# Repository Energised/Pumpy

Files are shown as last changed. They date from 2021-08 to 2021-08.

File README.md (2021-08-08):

# Design and Manufacture of a Syringe Pump

Research into Free Open Source Hardware (FOSH) has been extremely useful for academics and hobbyists alike. One such area includes the use of a basic linear actuator to create a rudimentary syringe pump. This has its uses in medical operations (palliative care/hospices/chemotherapy), chemical engineering (reactionware, chemical synthesis) and mechanical operation (life science, nanotechnology).

---
## Table of Contents

1. [Syringe Pump v1](./syringe-pump-v1/README.md)
   1. [Build Guide](./syringe-pump-v1/build-guide.md)
   2. [Modifications](./syringe-pump-v1/modifications-from-build.md)
2. [Syringe Pump v2](./syringe-pump-v2/README.md)
   1. [Build Guide](./syringe-pump-v2/build-guide.md)
3. [Electronics](./electronics/README.md)
4. [Testing Suite](./testing-suite/README.md)
   1. [Pump Operation Calculations](./testing-suite/pump-maths.md)
5. [Pump UI](./pump-ui/README.md)
   1. [Kivy GUI](./pump-ui/kivy-design/README.md)
   2. [PyQt GUI](./pump-ui/qt-design/README.md)
6. [Android Application](./android-app/README.md)
   1. [Pumpy App](./android-app/Pumpy/README.md)
   2. [Bluetooth Handler](./bluetooth-handler/README.md)

---
## Project Objectives

My main objective is to build a version of the Open Source Syringe Pump [1], adding several improvements from other projects that build upon it including:

* Upgraded Carriage for simpler bearing insertion and adjustable syringe holders
* Open syringe clamp for easy removal
* Limit switches for automatic position detection
* Ability to withdraw liquid automatically without removing the syringe
* Touchscreen interface using Python and PyQt 5 for basic user-friendly operation
* Android application to interact with the Syringe Pump via Bluetooth

I also plan to discuss the use of Free and Open Source hardware, the history behind medical syringe pumps and
the process by which we can build and program one with a touchscreen interface and Android remote operation for £150.

Overall I hope to show the process of utilising open source hardware and software to build and manufacture a product that rivals current consumer level technology, alongside providing a deliverable that could be put together and operated by a layman.

---
## What are Syringe Pumps?
Syringe Pumps (or Syringe Drivers) are battery powered pumps used to deliver medication into the body at a constant
rate. Patients are usually given them for a number of reasons:

* Nausea or Vomiting
* Difficulty swallowing oral medicine
* To avoid staff giving injected medicines frequently
* Unable to absorb medicines through their gut effectively

They are commonly used with patients receiving end-of-life care but are useful for managing the above symptoms
during any stage of care.

## Building a Pump

There exist many forms of the Open Source Syringe Pump that have been designed and released online. Having researched a number of these I decided upon 2 designs to work with and implement my modifications to. The STL files for 3D printing, BOM (Bill of Materials) and build guides are located in:

* syringe-pump-v1
  - Based on the Open Source Syringe Pump Library
  - Overhauls the electronics from the original design
  - Adds modifications to improve usability

* syringe-pump-v2
  - Upgrades to the Syringe Pump v1
  - Incorporates design elements from Andrey Samokhins design from Thingiverse
  - Larger side supports

The software to utilise each of these is still in development in the pump-ui and stepper-driver-code folders, but will
be combined into one piece of software with settings for both styles of pump.

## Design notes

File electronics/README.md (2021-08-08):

# Electronics for Syringe Pumps v1 and v2

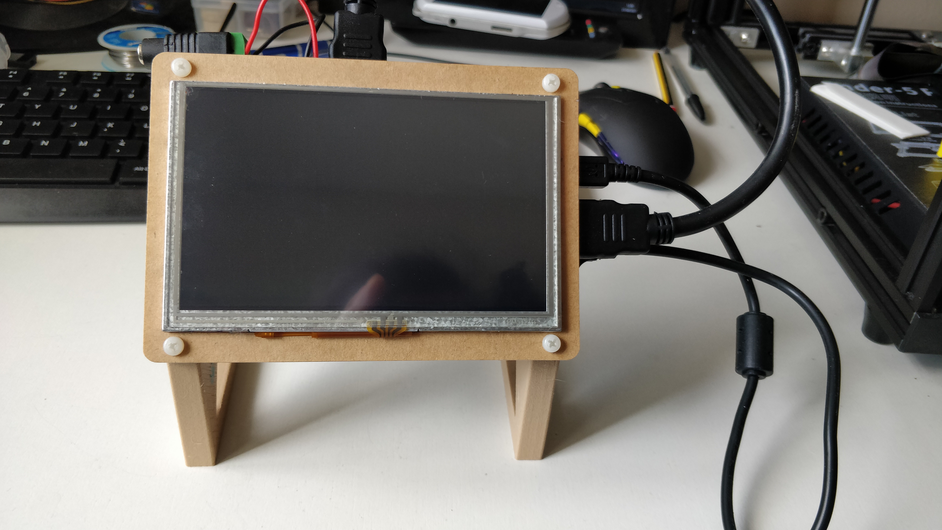
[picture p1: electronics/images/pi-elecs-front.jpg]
Front Image of LCD


To operate the pumps we require the following pieces of equipment:

* Microcontroller - Handles operation logic
* Motor Driver - To control the motor and talk to the microcontroller
* LCD Screen - Provides the User Interface and input
* Power Supply - 12V at 2A to run the motor and 5V at 3A for the microcontroller

For each of these I have chosen:

* Raspberry Pi

  - Powerful microcontroller running Raspbian Linux
  - Has built in Wi-Fi and Bluetooth for updates and remote operation
  - 40 GPIO pins for running external components
  - HDMI output for an LCD display

* A4988 Motor Driver

  - Easy to setup and operate
  - Cheap and powerful
  - Easily replaceable in case of failure

* Waveshare 5 inch LCD Touchscreen

  - Touchscreen capable for handling user input
  - Powered by the Raspberry Pi, no need for an external power source
  - Connects through HDMI and USB, doesn't use any GPIO pins

* 12V 2A Barrel Jack - Powers the Motor

* 5V 3A Micro USB - Extra current required to run Raspberry Pi and LCD screen

---
## Schematic for Syringe Pump v1

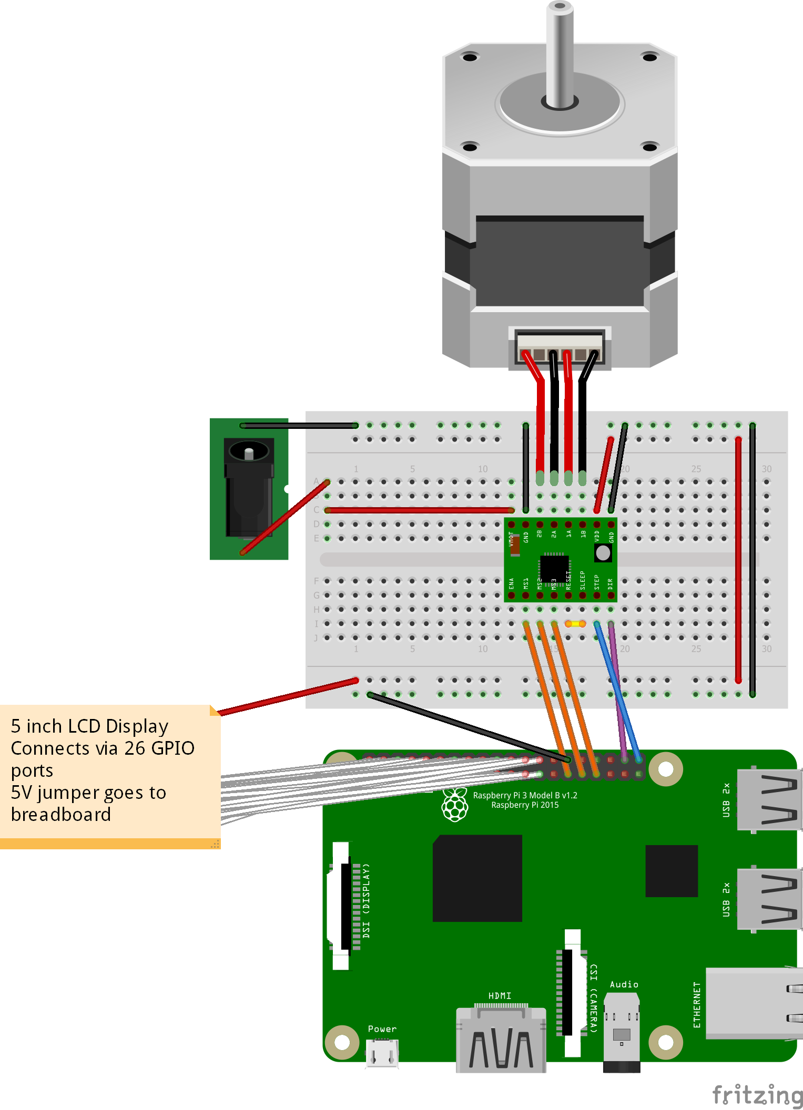
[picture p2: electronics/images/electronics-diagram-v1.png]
Fritzing Diagram for v1 Electronics


---
## Schematic for Syringe Pump v2

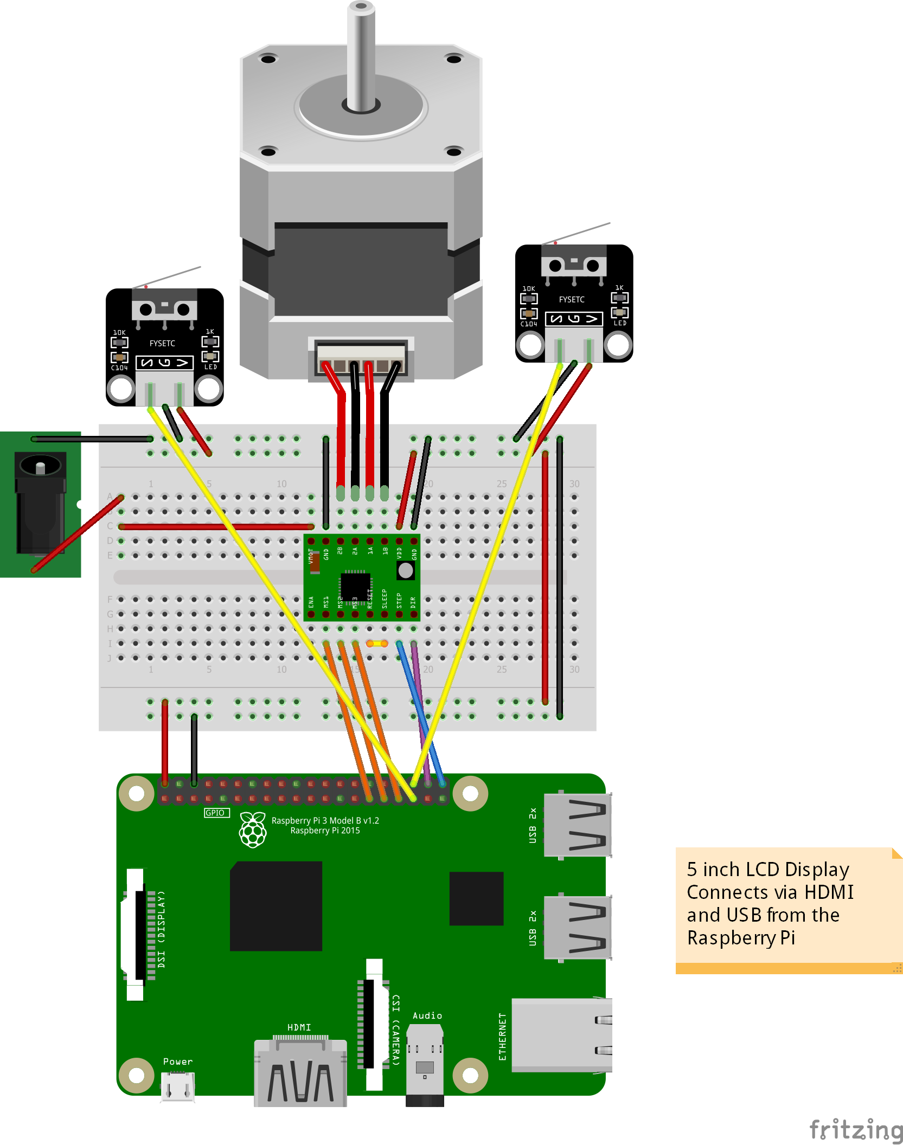
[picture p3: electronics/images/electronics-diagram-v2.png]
Fritzing Diagram for v2 Electronics


---
## Breadboard for v1 Setup

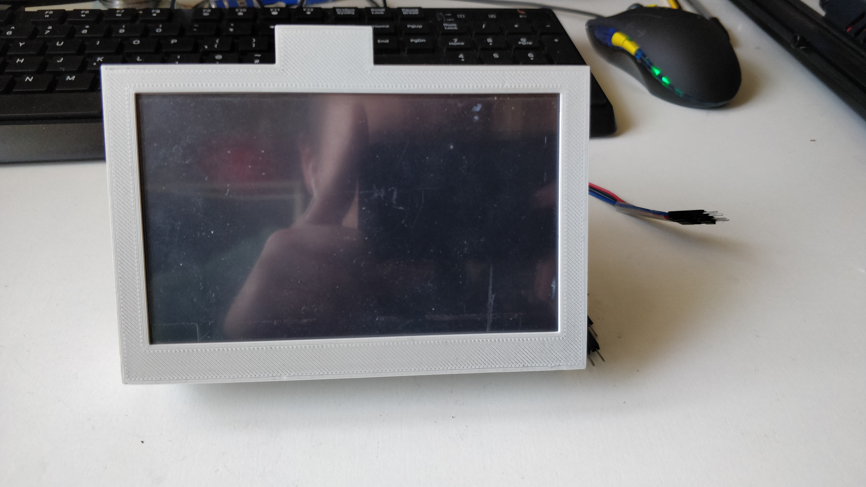
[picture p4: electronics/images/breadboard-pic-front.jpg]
v1 Breadboard with old LCD in 3D printed case

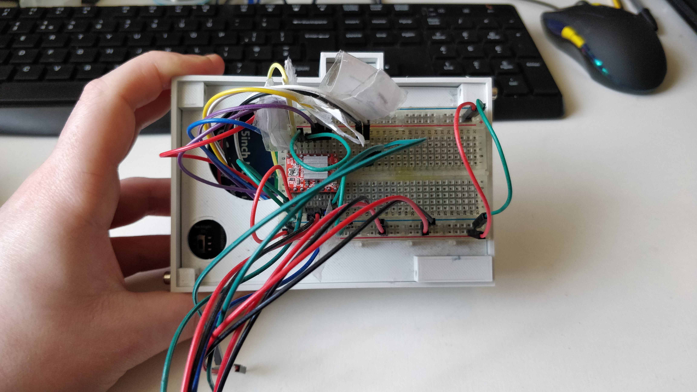
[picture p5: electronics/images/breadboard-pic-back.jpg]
v1 Breadboard system back


---
## Breadboard for v2 Setup

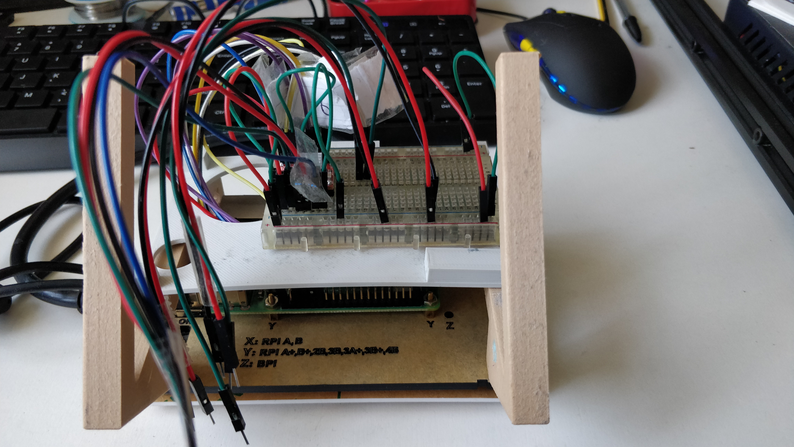
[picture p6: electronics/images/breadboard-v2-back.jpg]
v2 Breadboard back


---
## Final Electronics Setup for v2

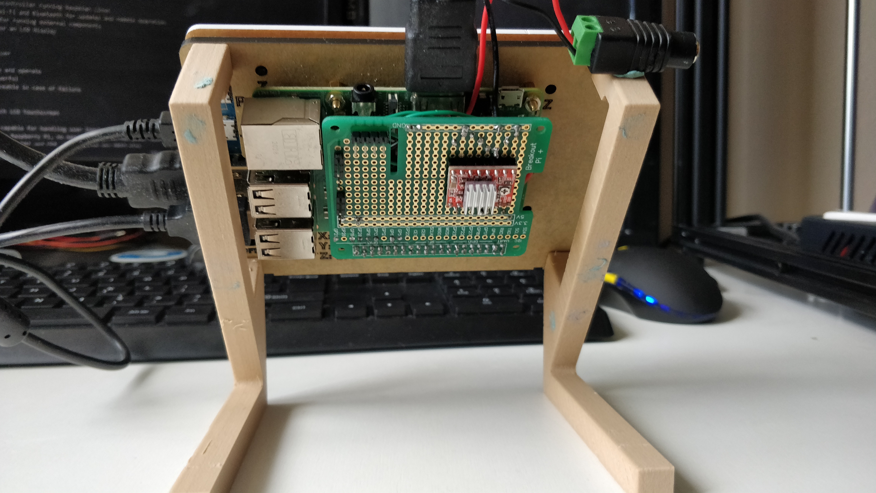
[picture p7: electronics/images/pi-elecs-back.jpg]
v2 Final Back


---
## Notes on Future Upgrades

* Design a PCB based on the breakout board
  - Will mean less soldering is required to build a complete system
  - Can allow for multiple motor drivers and limit switch headers to be installed
* Find a cheaper touchscreen alternative
  - One that makes use of the RPis onboard ribbon cable
* Combined Power Supply
  - 12V 2A for the Motor PSU
  - 5V 3A for the RPi PSU
  - Current system requires 2 power slots where I'd rather have 1

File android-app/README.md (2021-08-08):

# Pumpy - Android Application

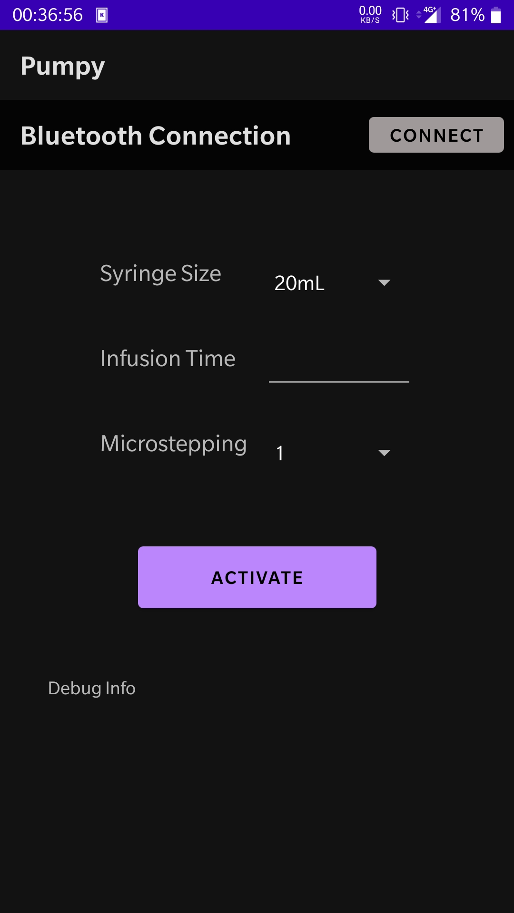
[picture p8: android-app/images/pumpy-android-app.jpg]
Android App Screenshot


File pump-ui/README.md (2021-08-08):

# Building a GUI for Pumpy

Now that we have:

* Upgraded version of the Pump hardware
* Electronics setup with microcontroller and touchscreen interface
* Testing suite for Pump operation
  - Including an object for handling multiple pump operations

We can create a graphical user interface (GUI) that provides all the required functionality
for our pump in a simple design that can be replicated for our Android application.

We've chosen to use Python as our programming language for its compatibility with the GPIO ports
on the Raspberry Pi. It also has a large number of GUI libraries we can make use of such as:

* Kivy
* Tkinter
* PyQt
* wxPython

Here I will discuss the 2 libraries I worked with: Kivy and PyQt5 and why I chose to use
PyQt5 for the final GUI system.

---
## Kivy

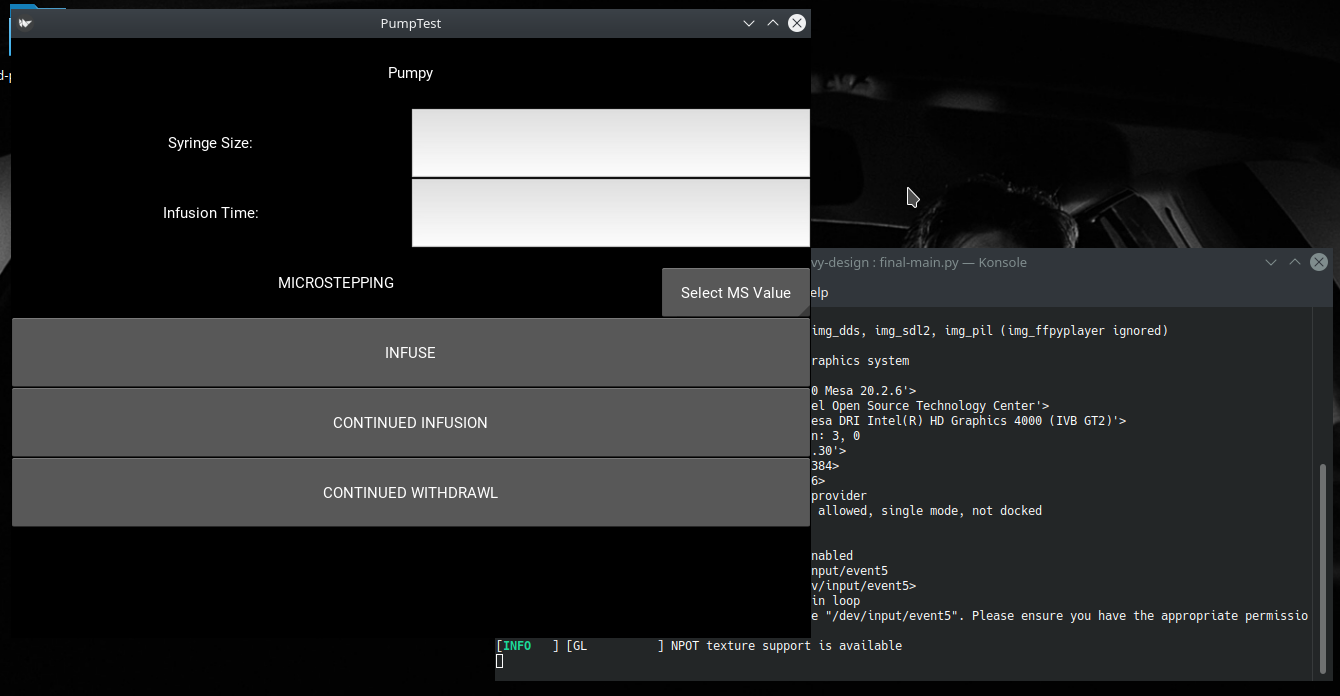
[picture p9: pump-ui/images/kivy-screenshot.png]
Image of Kivy GUI


Documentation for the code can be found [here](./kivy-design/README.md)

There are 2 main ways to design a GUI using Kivy:

* Write a `.kv` file for the UI elements and a `.py` file for the functionality
* Combine UI elements and functionality into a single `.py` file

Using a .kv file requires writing the UI structure in the Kv design language - a tool I
found to be unintuitive. It also allows for the separation of functionality and UI so that
the user can produce easy to read code.

Combining UI elements and functionality into a single file negates this benefit, allowing the
user to write code similar to the JSwing library for Java.

The main benefit of using Kivy is its ability to compile code into an executable Android application
for mobile devices. Doing this preserves the UI design across multiple platforms for consistency and
ease of use.

Unfortunately this also limits the functionality of the mobile application to simple I/O and as such would
be unable to operate the Syringe Pump. Due to this and the unintuitive nature of the Kv design language
I chose to build the application with PyQt5.

---
## PyQt5

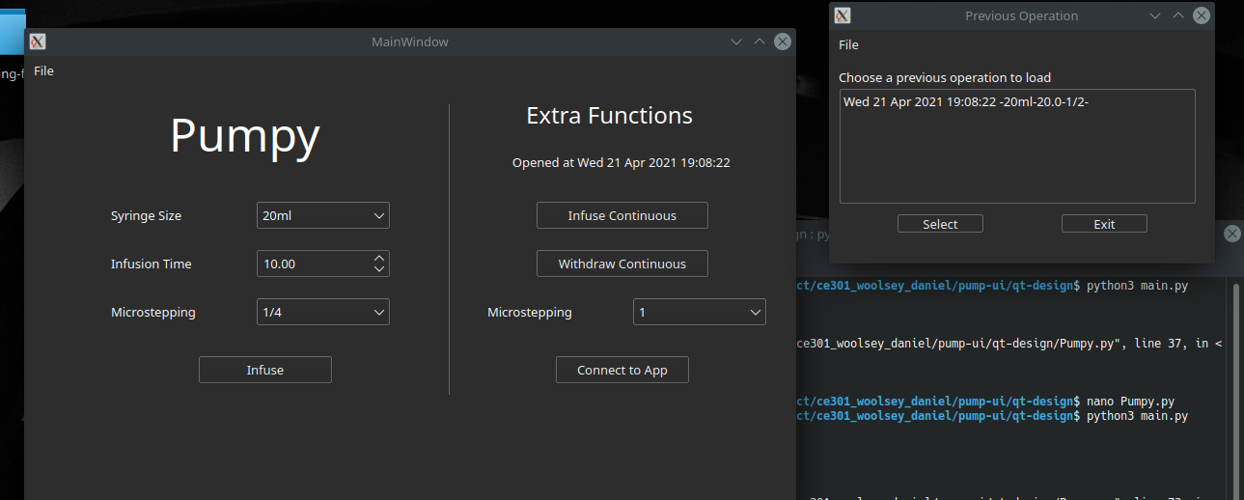
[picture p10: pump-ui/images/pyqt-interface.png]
Image of PyQt5 GUI


Documentation for the code can be found [here](./qt-design/README.md)

The Qt toolkit is a set of cross-platform libraries for software and UI design. The Python Qt library has a
number of tools that make designing UIs easier. For our purposes we use the Qt Designer application to create
a UI in the simplest way possible. This application generates a `.ui` file that can be imported into Python and
from there functionality can be written into the class.

This allows us the separation of UI elements and functionality that Kivy provided us with, but is much more
intuitive for designing a GUI. The Qt Designer gives you the maximum amount of control over how the GUI looks
with instant visual feedback and CSS support for styling elements.

Using this tool along with the PyQt5 library we have written a minimal GUI that is user friendly and adaptable
to mobile devices.

---
## Future Work

* Customisable syringe measurements for different syringe brands
  - Hospitals use a range of Syringe brands and my system is set for BD Plastipak syringes
  - UI would allow a choice of brands and rebuild the lookup table to reflect that
* Debugging tool for testing individual components
  - Would allow for a system where users can easily see what's wrong with their device
  - Very important for a tool designed for use by a computer layman

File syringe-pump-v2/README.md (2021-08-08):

# Syringe Pump v2

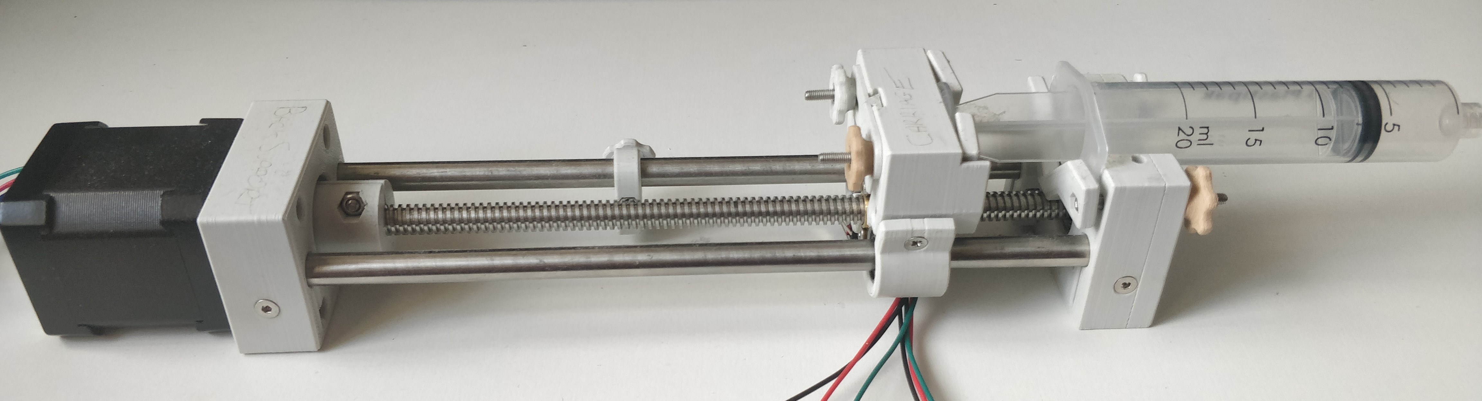
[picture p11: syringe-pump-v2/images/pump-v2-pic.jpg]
Syinge Pump v2 Image


## Introduction

The Syringe Pump v2 is an overhaul of the Open Source Syringe Pump used in Syringe Pump v1 and incorporates
design elements from Andrey Samohkhins Syringe Pump design [1]. This design brings in 2 extra features:

* Custom hand knobs for quick and easy syringe switching
* Limit Switches on the carriage to prevent over actuation
* Adjustable Limit Stoppers for easy withdrawl and setup of syringe

## Build Information

The model files for the 3D printed parts can be found [here](./stl-files) and were printed using an Ender 5 Pro printer. The bill of materials is included below:

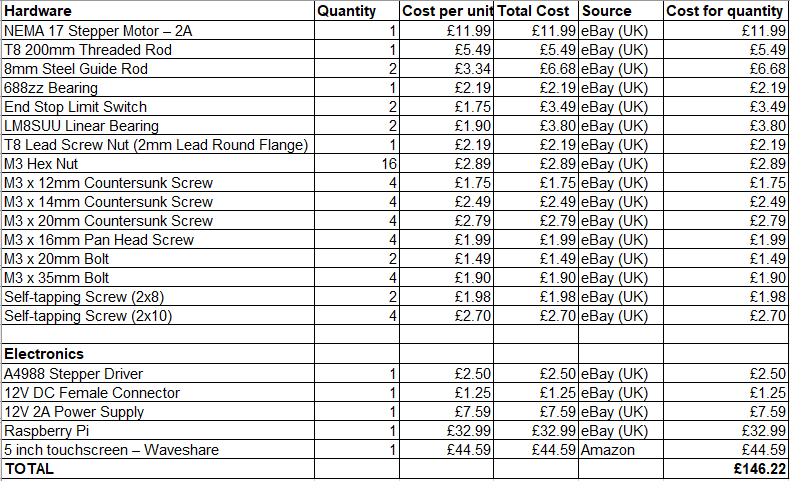
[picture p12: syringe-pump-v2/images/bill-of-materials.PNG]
Bill of Materials


There are a number of electronics requirements for building this pump:

* De-soldering Limit Switches from their breakout boards
* Cutting and soldering wires to each terminal of the Limit Switches

This is easily done with a soldering iron, wires, some solder and a bit of patience.

A [build guide](./build-guide.md) is included to account for modifications to the build guide initially written
for this style of pump. For the full electronics wiring diagrams please refer to the [electronics page here](././electronics/README.md).

## Future Modifications

* More robust hand knobs with locking systems for the bolts
  - Currently we're super gluing the bolts into the hand knobs, but it could be better
* Attachments on the side of the Motor and Idler ends to link with another Pump
  - Also requires extension of the electronics, Pump UI and mobile app

## References

[1] https://www.thingiverse.com/thing:4194094

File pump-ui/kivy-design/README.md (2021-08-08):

# Kivy Design

Screenshot of final-main.py

## `old_main.py`

This class was developed as a test system for trying out each of the UI elements required
for the Pumpy UI

### Functions

```
def forwards(instance)
def backwards(instance)
def release(instance)
```

Test functions to ensure that binding functions to elements works as intended

### Class

`def PumpTestApp(App)`

Main class to encapsulate all functionality and elements of the application. Subclasses the
App object from the Kivy library: `kivy.app.App`

### Methods

`def build(self)`

Overridden method inside of `PumpTestApp` that sets up 3 layouts:

* `main_layout`
* `middle_layout`
* `middle_left_layout`

Labels and buttons are setup inside of these layouts. `on_press` and `on_release` variables
for each button are set to the functions defined above. This method then returns `main_layout`
which is executed in the main function of the program.

### Main Method

```
if __name__ == "__main__"
    PumpTestApp().run()
```

The `run()` method of the App class will take the return value of the `build()` method and run
the layout through its graphics processing engine in order to generate the GUI we've described.

---
## `final-main.py`

Built to try a different layout style and build in the necessary features for the pump to be
operated

### Functions

```
def forwards(instance)
def backwards(instance)
def release(instance)
```

Test functions to be bound to buttons on the GUI

### Class

`def PumpTestApp(App)`

Main class that subclasses App and contains the methods for running the UI

### Variables

```
size_input = ObjectProperty()
time_input = ObjectProperty()
ms_button = ObjectProperty()
```

Objects to store widgets (UI elements) so we can call on them for the given user input or choices
for use by Pumpy.

### Methods

`def infuse(self, instance)`

Takes the given values for syringe size, time and microstep and displays them to the screen - these
values can easily be sent to Pumpy for infusion

`def show_spinner_value(self, spinner, text)`

Method for getting the value of a given spinner - a spinner is a clickable widget that allows the user
to input a number without typing

`def build(self)`

Sets up 4 layouts along with inputs for syringe size, microstepping and time input. Then buttons are set up
for infusion, continuous withdrawal and continuous infusion. The functions and methods above are bound to these
buttons and the UI returns the layout `main_layout`

### Main Method

```
if __name__ == "__main__":
    PumpTestApp().run()
```

The `run()` method of the App class will take the return value of the `build()` method and run
the layout through its graphics processing engine in order to generate the GUI we've described.

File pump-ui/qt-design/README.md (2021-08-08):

# PyQt Design

## `ui/pumpy-2.ui`

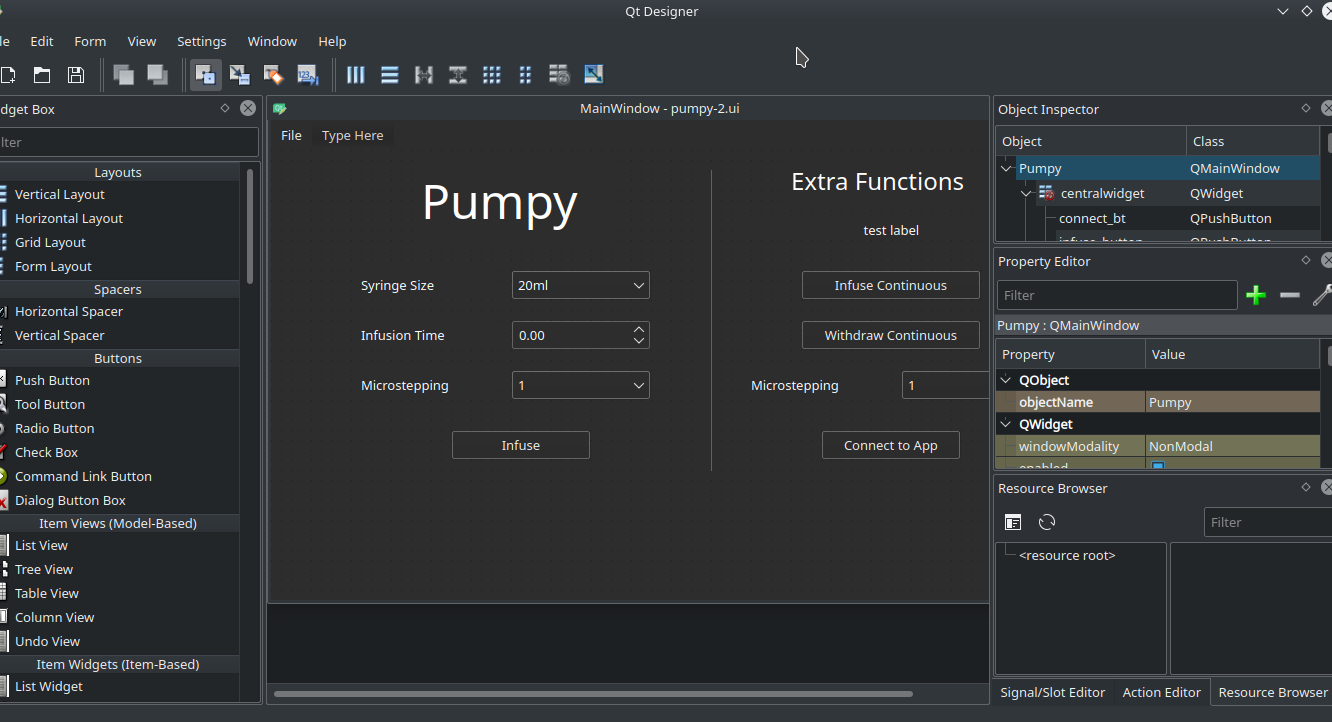
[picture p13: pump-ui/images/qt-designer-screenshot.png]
Image of Qt Designer


This is an image of the UI designed in Qt Designer - this is the second iteration I
wrote for this UI. Using stylesheets with Qt Designer brings some issues with elements
in the layout hierarchy so where the background should be grey it can show up white.

## `ui/prev_op.ui`

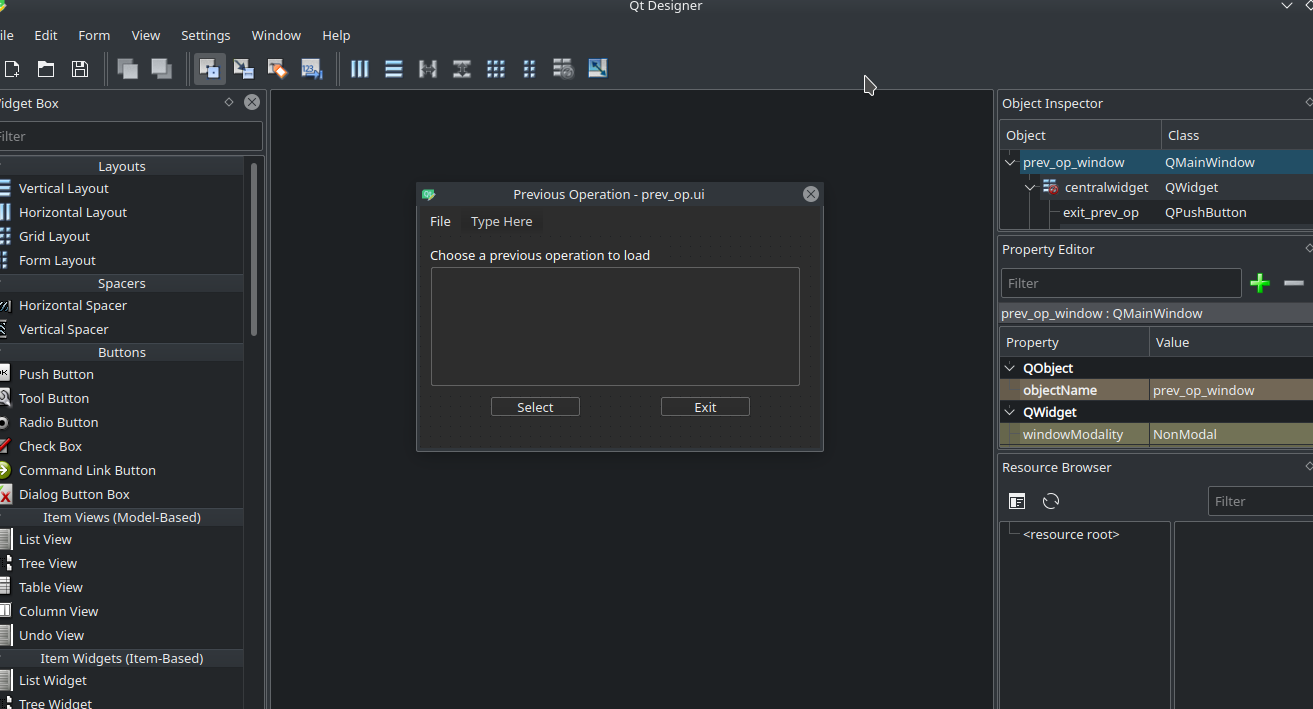
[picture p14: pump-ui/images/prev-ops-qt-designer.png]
Image of Qt Designer


Same issues as above were present, but this menu option is much simpler.

## `main.py`

### Classes

`class Pumpy_Ui(QtWidgets.QMainWindow)`

Handles importing the UI file, encapsulates the functions that the UI must perform and
assigns them to the correct buttons and text input elements.

`class PreviousOperations_Ui(QtWidgets.QMainWindow)`

Performs the same functions as above but for the Previous Operations screen

### Methods

For `Pumpy_Ui()`:
---

`def __init__(self)`

Imports the UI file `pumpy-2.ui`, sets up the Pumpy instance, connects functions to
appropriate buttons, sets up previous operations list and displays the window

`def infuse_button_pressed(self)`

Takes the user input values and calls `self.pump.pump()` with those values as
arguments - work is being done on a threaded alternative so that the GUI can
still be used while the pump is running

`def infuse_continuous_pressed(self):`

Takes the user defined micro-stepping value and runs the `self.pump.continuous()`
method for that value with `Pumpy.INFUSE` as the direction argument

`def withdraw_continuous_pressed(self)`

Takes the user defined micro-stepping value and runs the `self.pump.continuous()`
method for that value with `Pumpy.WITHDRAW` as the direction argument

`def open_prev_ops(self):`

Initialises the Previous Operations UI class and displays it to the screen

`def load_prev_ops(self, operation)`

When a previous operation is loaded in from the Previous Operations UI, this method
is called to setup the input boxes with the chosen operation

`def exit_ui(self)`

Closes the program by calling `sys.exit(0)`

For `PreviousOperations_Ui()`
---

`def __init__(self, parent)`

Load the Previous Operations UI file, bind functions to buttons and populate the
list of previous operations

`def load_operation(self)`

Gets the selected operation as a list and sends it to the `load_prev_ops(self, operation)`
method in `Pumpy_Ui()`

`def exit_ui(self)`

Closes the window by calling `self.close()`

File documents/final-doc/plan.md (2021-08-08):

# Final Document Planning
---
# Design and Manufacture of a Syringe Pump

## SECTION 1 - BACKGROUND

### Hardware

- 3D Printing
- Electronics
    - Raspberry Pi
        -
    - Motor Driver - A4988
    - NEMA 17 12V 2A Motor
    - Touchscreen
        - Choice of connection: GPIO, Ribbon cable, USB

### Software

- 3D Modelling
- Slicer
- GUI Library

### Medical Hardware

- Commercial Syringe Pumps
- Push for open source hardware (JOGL)
- Current Situation - COVID-19

## INVENTORY

All files I've worked on are included in this GitLab repository, will list below:

### Syringe Pump V1

- STL files (models) of each printed part
- Bill of Materials - all non printed parts and costs
- Datasheets for electronics
- Testing suite (pump_test.py - should separate file into 2 - one for each pump version)
- Build guide (on paper, to be written up in a markdown document)
- Modifications list I wrote to implement for V2

### Syringe Pump V2

- STL files (models) of each printed part
- Testing suite for extra functionality - limit switches to avoid chances of damage
- TODO: Write build guide

### Code
- Testing suite for both pump versions
- Pumpy - Pump operation handler class
- GUI 1 - Kivy version with pump operation code
- GUI 2 - PyQt5 version - better than Kivy, easier design process

### Electronics

- Breadboard version with Elecrow touchscreen
- Breakout board version with USB powered touchscreen (breakout board still failing :/)
- Breadboard with USB powered touchscreen - best alternative currently

## REFERENCES

Science - Pandemic brings mass vaccinations to a halt
Kheiralla et al. - Design and Development of a Low Cost Semi-Automated Poultry Vaccination Machine
Iqbal et al. - Automation of Vaccination and Blood Sampling Procedures
WHO. - Framework for decision-making: implementation of mass vaccination campaigns in the context of COVID-19
Gibson et al. - Vaccinate-assess-move method of mass canine rabies utilising mobile technology data collection in Ranchi, India
Amarante at al. - An Open Source Syringe Pump Controller for Fluid Delivery of Multiple Volumes
Kreiger et al. - Environmental Impacts of Distributed Manufacturing frm 3D Printing of Polymer Components and Products
Wijnen et al. - Open-Source Syringe Pump Library
Booeshaghi et al. - Principles of open source bioinstrumentation applied to the poseidon syringe pump system
Pearce - Quantifying the Value of Open Source Hardware Development
Dryden et al. - Upon the Shoulders of Giants: Open-Source Hardware and Software in Analytical Chemistry
Nature - Make nanotechnology research open-source
Baechler et al. - Distributed Recycling of Waste Polymer into RepRap Feedstock
Garcia et al. - Low-cost touchscreen driven programmable dual syringe pump for life science applications
Pusch et al. - Large volume syringe pump extruder for desktop 3D printers
Pearce et al. - Open-Source Wax RepRap 3D Printer for Rapid Prototyping Paper-Based Microfluidics

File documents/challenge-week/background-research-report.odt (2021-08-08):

CE301 – Design and Manufacture of a Syringe Pump

Background Research Report

BENEFITS OF OPEN SOURCE TECHNOLOGY

Open-Source technology has provided academics and hobbyists alike with the tools to bring their ideas to life. Tools such as RepRap [1] , Arduino [2], Apache [3] and Linux [4] have been instrumental in the widespread adoption of open-source in both free and commercial products since the early 1990s. The innovations bought about by these projects are widespread in modern day society: Android devices all have their roots in the Linux kernel, commercial 3D printer design is based on RepRap using Arduino-based control boards and 80% of the top 10 most accessed websites are running their servers on Linux [32].

Economists would have you believe that innovation comes solely from competition within markets: businesses competing to gain the largest profits by creating the best product. This point is antithetical to the philosophy of open-source development [5]. Open-source still allows for businesses to profit from open-source work, depending on the license type a project falls under, but the driving factor is innovation first and foremost – innovation coming from any individual/party with an interest in the research. With the internet allowing information to spread faster than ever before, open-source has the means to fully democratise information and prove that Isaac Newtons famous quote: “If I have seen further it is by standing on the shoulders of giants” is as true today as it was in his day [6].

FOSH (Free Open Source Hardware) has become a popular topic in the last decade, with 3D printing as a driving force to find cost-effective, reproducible solutions to areas such as specialised research equipment. Centralised repositories containing FOSH projects include the Open Hardware Repository [8] (created by CERN) and the dedicated journals HardwareX [9] and Journal of Open Hardware [10]. The greatest boundary to progress for FOSH comes from how a project is licenced. There are 2 classes of open-source licenses:

- Copyleft : Users can redistribute the original work or any derivative work as long as it uses the same license as the original work
- Permissive : Users can redistribute the original work or any derivative work under any license they choose

Copyleft licenses preserve the original works licence through any derivative work – that is work that modifies the original. On the other hand permissive licences allow redistribution of work in any setting: open-source or commercial. Permissive licences allow for large scale implementation of derivative work since the project can be run as a business while still preserving its open-source origins. The best example of this is the Android operating system whose open-source license allows for free application development and distribution – iOS on the other hand charge $99 per year for a developer license [33]. While somewhat counter-intuitive to the idea behind FOSH the proof is in the widespread adoption of Android with a 74% market share for all mobile devices [11].

FOSH requires a self-sustaining community to provide new points of innovation and collaboration – with certain individuals showing up more often. One such individual, Joshua Pearce, has been working in this community for over a decade with notable works such as: Open Source Syringe Pump Library [12], RepRapable Recyclebot [13], Wax 3D Printing for Microfluidics [14], Environmental Impacts of 3D Printed Products [15] as well as articles touting the benefits of adopting open-source in scientific fields such as nanotechnology [16]. His research has been cited over 15,000 times and has inspired many derivative works such as the project I am undertaking. He has written 2 books on the use of open-source technology and is on the editorial board for the journal HardwareX [9]. Without him the FOSH community and my own project would be very different.

3D PRINTING

Starting at the University of Bath back in 2005 the RepRap project intended to create a 3D printer that was low-cost and could print its own parts, eventually becoming a self-replicating machine. Before this project, a 3D printer would cost over £25,000 [1] and used a technique known as FDM (Fused Deposition Modelling) whose patent wouldn’t expire until 2009 [17]. This patent along with several others filed by Stratasys Inc. allowed the company to monopolise the manufacturing process, charging extortionate amounts for printers under a closed license. The expiration of the FDM patent allowed work from RepRap, Ultimaker and other businesses to be commercialised and brought down the cost of printers to £1000 and under [18].

3D printers can work with a variety of materials, most commonly thermoplastics such as PLA, ABS and TPU. A 3-axis gantry holds the extruder and 4 stepper motors controlling X, Y, Z movements and the pushing of material through the extruder. Models are designed using 3D modelling software (e.g. Blender, Maya, OpenSCAD) and run through a slicing program (e.g. Cura, Slic3r, Simplify3D) to generate Gcode – a human readable language instructing the machine where, when and how to move. This toolchain has enabled users – both beginners and experts – to build anything they can design. Websites such as Thingiverse and Youmagine are repositories for model files, allowing users to ‘remix’ the designs they find to suit their own projects and reinforces the open-source platform that RepRap was first build on.

Thermoplastics are just one of many materials 3D printers can be configured to work with. TPU is an example of a flexible thermoplastic, suiting designs that require strong and bendable moving parts. RepRap based printers have been modified to print wax (removing a large number of cost and time intensive processes) [14], hydrogels through syringe pumps that replace the extruder on a regular 3D printer [20], liquid catalysts for small scale 3D printed reactors with comparable purity to traditional glassware reactors [21] and so called ‘smart materials’ such as electroactive polymers that change their size or shape when stimulated by an electric field for fluid motion in robotics [22].

Another factor to consider is the environmental impact of 3D printing. Waste plastics account for 5 million tonnes of waste every year in the UK alone [23] taking hundreds of years to decompose: polluting soils, rivers, oceans and harming animals. The process of upcycling waste plastic has come in many forms: most notably the creations of Spiral and Joyxee Islands, pieces of land supported by around 100,000 plastic bottles [24]. In the context of 3D printing the concept of RecycleBots have gained traction since 2013, which involve the shredding of household plastics (e.g. milk and water bottles, laundry detergent bottles) and extruding them into usable 3D printing filament with a diameter margin of error of <5% [13]. This brings the estimated cost of filament to 2.5 cents per/kg (< 2 pence), less than 1000x the cost of commercial filament. The device itself costs less than $700 (roughly £540), but the return on investment and reduction of individual carbon footprint heavily outweigh this starting cost.

The future of 3D printing hinges on the community of makers working together to show the benefits of this technology to the consumer. Reddit has many useful communities doing this already, such as those dedicated to: helping solve printing issues (/r/fixmyprint), advertising practical prints (/r/functionalprint), advice for every brand of commercial printer (/r/ender3, /r/prusa etc) and lengthy posts detailing the process of choosing a printer all the way to calibration for micrometer-accurate prints [34]. Having bought an Ender 5 Pro for use in my project, the maker community has been a crutch for solving issues I would otherwise have spent days trying to work out myself.

RELATED RESEARCH

Syringe/Infusion Pumps are programmable linear actuators that push a syringe plunger with a set torque over time using a stepper motor. Most stepper motors perform 200 steps per revolution (meaning each step is equivalent to 1.8 degrees) and can be programmed to use microsteps, upping this value to 3200 steps per revolution. Flow rate (usually mesured as micro litres/second) can be calculated theoretically and the pump calibrated to compare actual liquid infused [26]. These devices are simple in concept but must conform to strict health and safety standards before use in a medical setting [35]. For this reason, companies manufacturing these pumps can charge from £300 to over £2000. In a research setting this upfront cost may seem extortionate for a closed-source and difficult to modify piece of equipment. Open-source research into syringe pumps has put the cost to fabricate a custom pump at under £100 [12]. Since the Open-Source Syringe Pump Library (OSSPL) was first released in 2014 its design has been downloaded over 8000 times [27] and many papers exist creating novel uses for it.

Appropedia was used to setup a page detailing the OSSPL and includes a bill of materials along with instructions for building one yourself [19]. As a result a number of modifications were designed and linked to the main project page such as the Lynch modifications [25] which give the pump features similar to those of a commercial pump. Unfortunately the software library the project uses is deprecated and doesn’t run, so we must look at other projects for an operational analysis of the product.

Two such projects exist and I plan to utilise aspects from both that fit with my concept of an open-source syringe pump:

The low-cost touchscreen driven programmable dual syringe pump (PDSP) is designed for laboratory applications – namely for (in laymans terms) breaking down cells into lysates (liquid protein from cells) for analysis, a process that would ordinarily be done by hand [26]. The design of the syringe pump is inspired by the OSSPL with a focus on user interaction via a touchscreen interface. The paper contains a great deal of information on the building process, making effective use of images to help guide anyone attempting to replicate the project. The design is extensible through the use of the PiPlates MotorPlate: on its own capable of controlling 2 stepper motors, extended up to 16 stepper motors by adding more MotorPlates for larger scale systems. The printed design files and software are easily available online, with the interface being easily re-designable with a basic knowledge of Python and Tkinter. From this project I hope to utilise a similar touchscreen interface and provide a similar option for the addition of more pumps.

The Poseidon syringe pump and microscope system is designed for microfluidics experiments – infusing liquid in the order of tens of microns in size [28]. The combination of syringe pump and microscope is for performing basic light microscopy (visualising fine details by focusing a beam of light through a series of glass lenses). The syringe pump itself operates through an Arduino while the microscope operates through a Raspberry Pi, with data being sent via serial communication between the 2 devices to operate the pump on the Pi. From my experience, this can be a slow and impractical method of controlling a motor and is not something I would utilise. The paper uses the Poseidon system to illustrate open-source design principles including: Functionality, Robustness, Safety, Simplicity, Modularity, Benchmarking and Documentation. This is an excellent method of describing an open-source project and I plan to follow the same set of principles with my own work. The design files and code are available on their Github page [29] and includes videos, testing data and the ability to raise issues via Github for easy modification and integration into the project. The principles this project follows should be mandatory for any open-source project.

More trivial concepts have been realised based on the OSSPL such as the 8ARM: Open Source Precision Pump [30] – an interesting take on using syringe pumps and mechatronics to create a robotic bartender capable of mixing drinks to a degree of accuracy no human could recreate even with an error of 1 +- 0.05 cL. While an amusing concept, in practice there are many environmental variables the designer cannot account for. There is also a YouTuber known as Dr D-Flo who designed and build a ‘3D Food Printer’ [31]. This system is a CNC gantry with a syringe pump as an extruder that pipes icing onto a cake or large cookie. Initially using the CNC gantry for a larger print area, he encountered problems using NEMA 23 motors with a stepper driver that couldn’t provide enough current. The project hasn’t been fully realised, but would be an interesting project for independent cake businesses to get an edge over their competition.

REFERENCES

[1] The RepRap Project https://reprap.org/wiki/ (https://reprap.org/wiki/About)A (https://reprap.org/wiki/About)bout (https://reprap.org/wiki/About)

[2] Introduction to Arduino https://www.arduino.cc/en/Guide/Introduction

[3] Apache HTTP Server Project http://httpd.apache.org/

[4] The Linux Foundation https://www.linuxfoundation.org/about/

[5] The Open Source Definition https://opensource.org/docs/osd

[6] Dryden et al. Upon The Shoulders of Giants: Open Source Hardware and Software in Analytical Chemistry Anal. Chem. 2017, 89, 4330-4338

[7] Pearce, J M – Open Source Lab (2013) – ISBN: 978-0-12-410462-4

[8] Open Hardware Repository (CERN) https://ohwr.org/welcome

[9] HardwareX – Elsevier - https://www.journals.elsevier.com/hardwarex

[10] Journal of Open Hardware - https://openhardware.metajnl.com/

[11] Mobile OS Market Share (Accessed October 2020) - https://gs.statcounter.com/os-market-share/mobile/worldwide

[12] Wijnen et al. - (2014) – Open-Source Syringe Pump Library

[13] Woern er al. - (2018) - RepRapable RecycleBot: Open Source 3D printable extruder for convering plastic into 3D printing filament

[14] Pearce et al. - Open Source Wax RepRap 3-D Printer for Rapid Prototyping Paper-Based Microfluidics

[15] Kreiger et al. - Environmental Impacts of Distributed Manufacturing from 3D Printing of Polymer Components and Products

[16] Pearce J – Nature Vol. 491. 519-521- Make nanotechnology research open-source

[17] FDM Patent – Stratasys Inc - https://patents.google.com/patent/US5121329

[18] https://medium.com/@erinwinick/3d-printings-30-year-history-and-why-it-is-popular-now-5200ab21a7ed

[19] https://www.appropedia.org/Open-source_syringe_pump

[20] Pusch et al. - Large volume syringe pump extruder for desktop 3D printers

[21] Combining 3D Printing and Liquid Handling to produce User-Friendly Reactionware for Chemical Synthesis and Purification

[22] Liu et al. - 3D Printing of Smart Materials: A review on recent progresses in 4D printing

[23] https://commonslibrary.parliament.uk/research-briefings/cbp-8515/

[24] https://www.atlasobscura.com/places/joyxee-island

[25] http://www.appropedia.org/Lynch_open_source_syringe_pump_modifications

[26] Garcia et al. - (2018) – Low-cost touchscreen driven programmable dual syringe pump for life science applications

[27] Syringe Pump STL Files - https://www.youmagine.com/designs/syringe-pump

[28] Booeshagi et al. (2019) – Principles of open source bioinstrumentation applied to the poseidon syringe pump system

[29] Poseidon Syringe Pump System – Github - https://github.com/pachterlab/poseidon

[30] 8ARM: Open Source Precision Pump https://www.diva-portal.org/smash/get/diva2:915985/FULLTEXT01.pdf

[31] Dr D-Flo – 3D Food Printer - https://www.drdflo.com/pages/Projects/3D-Food-Printer.html

[32] https://peacocksoftware.com/blog/what-server-os-are-top-sites-running-2020

[33] https://developer.apple.com/support/compare-memberships/

[34] https://www.reddit.com/r/3DPrinting/wiki/gettingstarted

[35] https://www.fda.gov/media/116949/download

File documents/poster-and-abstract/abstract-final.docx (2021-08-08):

Project Title: Pumpy – Design and Manufacture of a Syringe Pump

Student: Daniel Woolsey

Supervisor: Nick Zakhleniuk

Abstract.

Due to COVID-19, medical equipment and PPE have been in short supply and high demand. For the first time hospitals relied on individuals to 3D print face masks to handle the growing supply concerns they faced. This has the potential to be applied to other forms of medical equipment such as syringe pumps, which provide continuous, hands-free drug delivery and can cost more than £1500 per unit.

In this project we designed, 3D printed and built a medical-use syringe pump and computer interface based on Joshua Pearce’s Open Source Syringe Pump. We programmed both a touchscreen interface for a Raspberry Pi computer and an Android application for remote operation via Bluetooth.

We have demonstrated that medical-use syringe pumps can be built for less than 10% of their market value. This open-source approach to manufacturing equipment can allow hospitals to handle supply issues internally and can help to provide inexpensive medical equipment to poor areas with limited modern technology.

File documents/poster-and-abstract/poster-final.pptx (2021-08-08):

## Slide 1

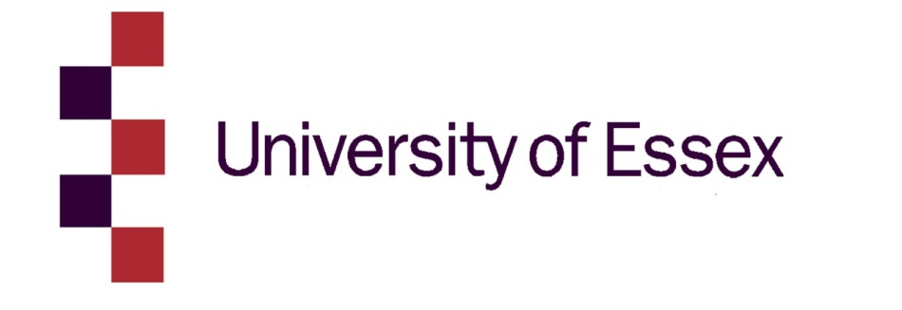
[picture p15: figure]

Pumpy
Design and Manufacture of a Syringe Pump

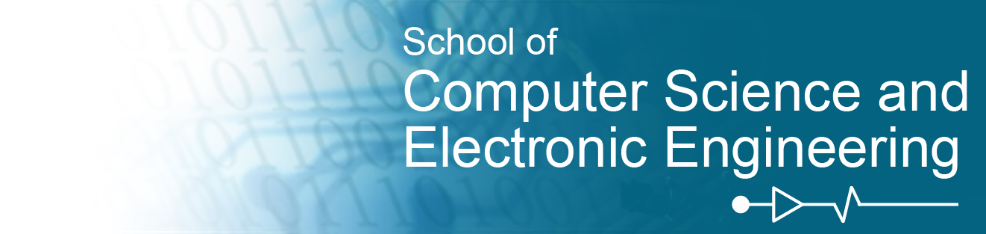
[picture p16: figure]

Student: Daniel Woolsey
Supervisor: Nick Zakhleniuk

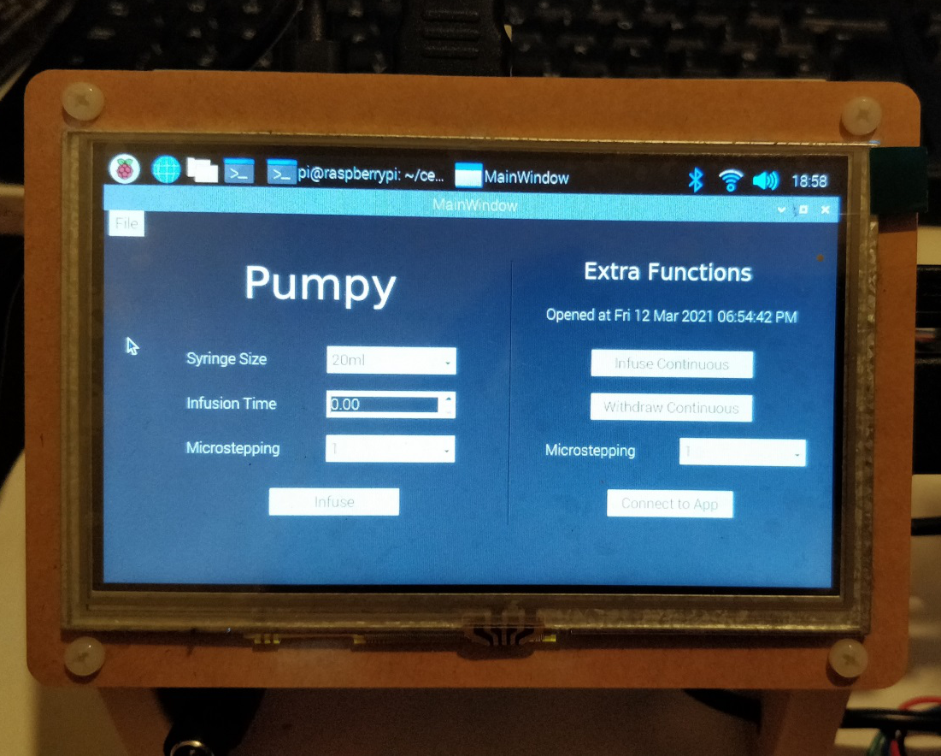
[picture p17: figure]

- Stepper motor for precise movement
- Mostly 3D printed parts to reduce cost
- Hand knobs for easy syringe replacement
- Limit switches on the carriage prevent
damage to the pump

AIM
To build a touchscreen ready, mobile phone controlled, cost-efficient, open source Syringe Pump for a real-world medical applications (estimated costs under £150)

BACKGROUND
- Typical medical-use Syringe Pumps cost > £1000
- Medical equipment is in short supply due to COVID-19
- Open-source Syringe Pumps have only been used in bespoke labs
- 3D printing has paved the way for democratised production
- Eventually, hospitals could print their own equipment
- The approach and the product can be used in areas with limited access to modern technology

- Minimal User Interface
- Wi-Fi and Bluetooth
Compatible
- Powered by a Raspberry
Pi computer
- Touchscreen interface
- Stored backlog of previous
operations

Android application for remote
pump control

Connects to the Raspberry Pi
over Bluetooth

All remote operations are stored
on the pump

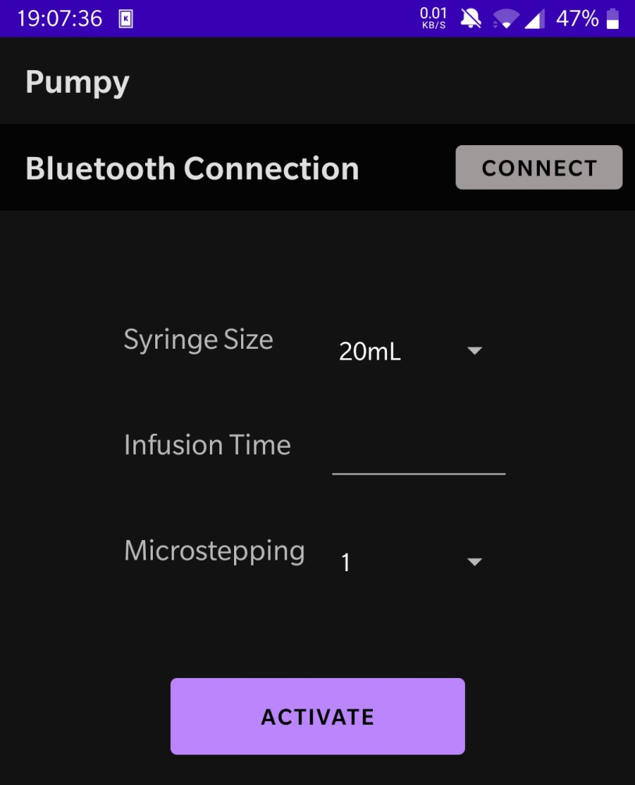
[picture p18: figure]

RESULT
We have demonstrated and implemented a 3D printing-based approach to the manufacture of Syringe Pumps for a variety of medical applications

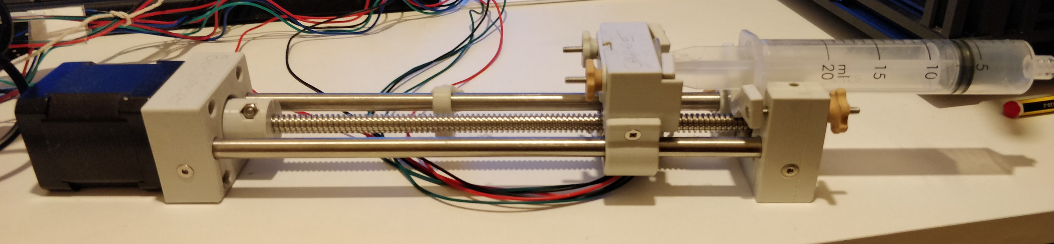
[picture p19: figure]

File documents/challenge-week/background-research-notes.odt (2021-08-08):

notes:

section 1:

- Bringing manufacturing and design to the consumer
- Widespread adoption of popular open source projects
  - RepRap [https://reprap.org/wiki/Wealth_Without_Money]
  - Arduino [https://www.arduino.cc/]
  - Apache [https://www.apache.org/theapacheway/index.html]
  - These have been implemented in both FOSS/FOSH projects as well as consumer products licenced under a permissive license agreement
- Innovation doesn’t come from market competition alone
  - Freedom of information allows for a wider community to become part of the innovation process
  - [Open Source Lab + Upon the Shoulders of Giants]
- Open source licenses exist to explicitly inform users what they can do with the project
  - Copyleft vs Permissive
    - Production of application binaries for commercial use based on open source work
- Patent filing is the greatest hindrance to progress in Open Source communities
  - [Make Nanotechnology research Open source]
  - Large number of Syringe Pump patents filed, lasting 15 years
- Big thanks to Joshua Pearce – Open Source hardware pioneer, contributed to hundreds of projects and articles
  - [Make nanotechnology research open source]
  - [Open Source Syringe Pump Library]
  - [RepRapable Recyclebot]
  - Work on quantifying the value of Open Source Technology
    - Provides a mathematical model for calculating market value in 3 areas
      - Downloaded Substitution Valuation
      - Avoided Reproduction Valuation
      - Market Savings Valuation
    - Alongside a case study: applying this model to the OSSPL along with projected figures for 2019
      - Can calculate this myself in 2020 and compare my findings to his predictions

section 2

  - RepRap project
  - Open source project from Uni of Bath
  - Began February 2004
- Use of varied printing materials
  - PLA/ABS – standard plastics
  - NinjaFlex, Ferrofluids, carbon fibre – next stage of consumer manufacturing
    - 3D printing of smart materials, 4D printing, ferromagnetic domains
    - Sources from previous project on Smooth Surface Generation
- 3D Printing + Liquid Handling for User Friendly Reactionware
  - Modified a printer to extrude a liquid catalyst
  - Printed the reactor casing, printed in the catalyst, then printed the rest of the case
  - Done with 2 printers, a syringe pump mounted on a gantry could achieve a similar result
- RepRapable Recyclebot
  - Turning household plastics (milk/water bottles, detergent bottles) into usable filament for a 3D printer
  - Improvements in the technology over the last 7 years – see [J Pearce – RepRapable Recyclebot + Distributed Recycling of Waste Polymer into RepRap feedstock]
  - [Environmental Impacts of Distributed Manufacturing from 3D printing of polymer components and products]
- Open Source 3D printing of OSAT (Open source appropriate technologies) (2010)

section 3

- Touchscreen idea for intuitive user interface
  - [Low-cost touchscreen driven programmable dual syringe pump for life science applications]
- Poseidon Syringe Pump System
  - Biological applications stemming from the RepRap project
  - Microfluidic devices
- Individuals building and improving on the OSSP project [1 Open Source Syringe Pump Library 2014]
  - Appropedia for user designed modifications [Lynch Open Source Pump Modifications]
  - Choice between microcontrollers and motor control boards – Raspberry Pi vs Arduino, A4988 vs DRV8825
  - Benefits of microstepping – accuracy increase? [Hackaday article on microstepping]
- Open-Source Wax RepRap 3D Printer for Rapid Prototyping Paper-based Microfluidics
  - Removing the need for other more time intensive processes (lithography, etc (see paper))
- Large Volume syringe pump extruder for desktop 3D Printers
  - Modification available for any commercial/RepRap 3D printers
  - Applying a different area of science (hydrogels) to the concept of the Syringe Pump
    - Shows how versatile the concept is
- Trivial projects
  - 8ARM: Open Source Precision Pump for bartending
  - 3D Food Printer – Youtuber Dr D-Flow – Syringe Pump attached to gantry for icing cakes/pies

section 4

(probs gonna ignore this section for now, will add to final document)

MARKET ANALYSIS

- Patent filing (get exact figures)
- Market Value for Infusion Pumps and Syringe Pumps (get figs)
- Compare the market to 2014
  - [Quantifying the Value of Open Source Hardware]
- Number of Syringe Pump projects started since 2014 with OSSPL
- PHDUltra Syringe Pump – Harvard Apparatus
  - Marketed with touchscreen – build isn’t modular, touch to customise
  - Software is a black box, no ability to modify code

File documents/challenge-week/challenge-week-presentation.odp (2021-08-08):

## Design and Manufacture of a Syringe Pump

Daniel Woolsey

## Project Objectives

- Improve upon the Open Source Syringe Pump Library
  - Take inspiration from commercial pumps and other projects
- Allow for easy extensibility into dual pump system
- Add the ability to withdraw solutions into the pump
- Design touchscreen interface for ease of operation
- Compare accuracy of different stepper motors and the benefits of micro-stepping
- Current market analysis of Syringe Pumps
  - Compare to predictions made in case study from ‘Quantifying the Value of Open Source Hardware Development

## Project Objectives

- Develop an Android application as another means of operation
- Display use of Jira and the KanBan methodology in developing a project
  MOST IMPORTANTLY
- Show the process of developing an open-source project
  - Best practices to follow
  - Following 7 key design principles

## Design Principles

- Functionality – Develop for an application
- Robustness – Design with variation in mind
- Safety – Communicate hazards to users
- Simplicity – Make easy to source, build and operate
- Modularity – Build independent and individual units
- Benchmarking – Validate with standard protocols
- Documentation – Describe the design completely

## Implementation Plan

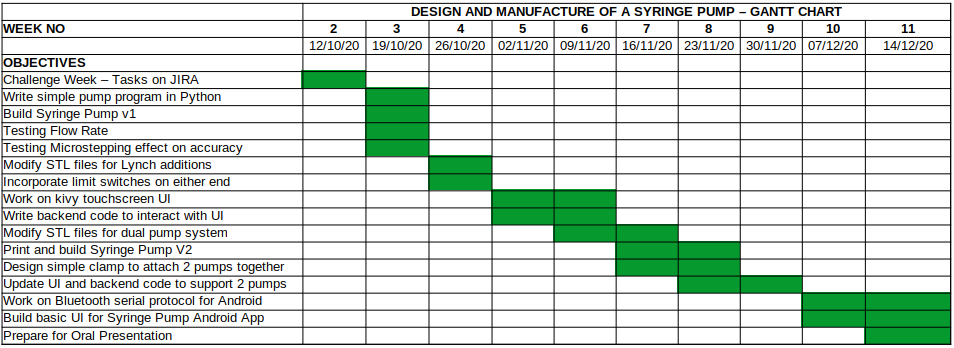
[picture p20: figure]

## Risks

- Lack of novel hardware design changes
  - Software will be novel
- Damage to equipment
  - Everything is cheap and easily replaceable
- With more modifications, project loses simplicity
  - Keep everything modular, get a layman to build and operate the SP based on written documentation

## Context

- Commercial Lab equipment is expensive and unsuitable for modification
  - Open source is inexpensive and (usually) designed with modification in mind
  - The quality of commercial syringe pumps is easily achievable at a low cost
- Updating design for the modern-day user
  - Mobile phones are widespread and easily understood by most everyone
  - Build an interface to reflect mobile app design principles for HCI

## Context

- Quantifying the Value of Open Source Hardware Development
  - In 2014, predictions made about the future of the Syringe Pump market
- Latest Syringe Pump Projects
  - PDSP – Evolved UI and extensibility
  - Poseidon – Focus on micro-fluidics and open-source design principles, strong documentation

## Achievements during Challenge Week

- Applying KanBan methodology to daily project tasks
- 3D printed parts for Syringe Pump and ordered all items on the Bill of Materials
- Timeline of objectives up until Week 11
- Completed Analysis of Related Works for Background Reading

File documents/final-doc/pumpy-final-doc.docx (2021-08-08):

Pumpy – Design and Manufacture of a Syringe Pump

Student: Daniel Woolsey

Supervisor: Dr Nick Zakhleniuk

Second Assessor: Dr Vishuu Mohan

BSc Computer Science

University of Essex

2021

I would like to thank my family and friends for their invaluable support throughout this difficult year.

A big thank you to my supervisor Dr Nick Zakhleniuk whose weekly meetings and consistent guidance helped bring this project to where it is now.

Finally, I’d like to thank the open source community, who have provided resources for anyone to learn and utilise new and interesting technology.

Due to COVID-19, medical equipment and PPE have been in short supply and high demand. For the first time hospitals relied on individuals to 3D print face masks to handle the growing supply concerns they faced. This has the potential to be applied to other forms of medical equipment such as syringe pumps, which provide continuous, hands-free drug delivery and can cost more than £1500 per unit.

In this project we designed, 3D printed and built 2 medical-use syringe pumps based on Joshua Pearce’s Open Source Syringe Pump. We programmed both a touchscreen interface for a Raspberry Pi computer and an Android application for remote pump operation via Bluetooth.

We have demonstrated that medical-use syringe pumps can be built for less than 10% of their market value. This open-source approach to manufacturing equipment can allow hospitals to handle supply issues internally and can help to provide inexpensive medical equipment to poor areas with limited modern technology.

Medical equipment is always in demand yet remains in a status quo – startups with new ideas must work with large corporations to make them a reality. This is due to the difficulty of creating equipment that meets with the approval of regulatory boards worldwide. Large corporations can monopolize specific parts of the market and charge extortionate premiums to the healthcare system that needs it. For example, Johnson and Johnson (JNJ) acquired Auris Health for their Monarch endoscopy robotic system for $3.4 billion [1]. Such a device will become commonplace in hospitals over the next decade but was only able to reach FDA approval after the JNJ acquisition.

Modern equipment like Monarch is a true vision of the future but ignores a huge problem the medical equipment sector faces – the mismatch problem. Outlined in a WHO report from 2010, it explains that the medical equipment industry invests more in R&D for equipment that will only be used in 1st world countries rather than creating accessible, affordable and appropriate equipment for use in low-resource settings [2]. The report hypothesizes that a countervailing force must focus the medical device market towards public health considerations at all stages of the device lifecycle. I believe that open source hardware can be that force.

During the COVID-19 pandemic we saw waves of medical equipment shortages in hospitals worldwide. This led to several open source initiatives allowing individuals to help provide PPE to medical staff such as 3DCrowd [3] and the NIH 3D Print Exchange [4]. Coupled with research into the adoption of open source hardware for diagnostic tools and ventilators [5], we saw hospitals begin to produce their own reusable PPE in-house [6] to handle the supply chain issues they faced. Having seen the benefits of 3D printing and open source hardware in hospitals, there is a chance that open source can be a new norm in the medical industry.

The open source ecosystem is, by nature, decentralized and democratic [7], which goes against many business practices where ideas are patented, and their inner workings are hidden trade secrets. The switch to open source brings product development to the people, with democratic decision making leading to rapid innovation. We’ve seen this with software like Linux, Android, and Arduino – all of them open source projects used in commercial products and provide a better experience for both developers and consumers.

When applying the open source methodology to more complex medical equipment than PPE we are faced with a big issue – regulation. Medical authorities such as the FDA provide resources for manufacturers to follow when attempting to get a device approved for use [8]. Applying this approval process to open source where change and innovation are prioritized is a challenge, since any revisions will have to be re-approved. To overcome this, any open source medical device requires a medically approved baseline with changes approved by committee in regular intervals.

In this paper I want to analyze and build upon an already existing open source baseline for a complex medical device – a syringe pump. Syringe Pumps (also known as Infusion Pumps or Syringe Drivers) are motorized linear actuators that deliver medicine to a patient at a constant rate over a 24-hour period [9]. They are commonly used for patients who have trouble taking medication orally or are in end of life care.

The main goals of this paper are as follows:

- To analyze, build and test a current open source Syringe Pump
- Modify and improve the hardware
- Design an electronics system for user friendly operation
- Create a mobile application for remote pump operation
- Explore the viability of a cheap and open source medical Syringe Pump solution

In Section 2 I explore the background of the main areas the project concerns: Syringe Pumps (both commercial and open source), Open Source technology, 3D Printing and the medical uses of Syringe Pumps along with their issues. Section 3 shows my technical documentation for the project hosted on Gitlab. Section 4 explains how I approached each stage of hardware and why I chose the solutions I did. Section 5 describes my approach to software – the chosen programming language, libraries I decided upon and how they were utilized. Section 6 details the process of my work from building the first prototype to creating a final solution. Finally, in Section 7 I discuss the results and performance of my Syringe Pump system, the project planning and development strategies I used, the benefits and weaknesses of open source development and the future viability of open source medical devices.

This project builds upon previous Syringe Pump projects with a focus on using open source hardware and modern manufacturing processes to bring cheaper medical equipment to the healthcare industry. Below I discuss the main aspects of my project: Syringe Pumps, Open Source, 3D printing and the history of medical Syringe Pumps.

# 2a. Syringe Pumps

Syringe Pumps are used in a variety of contexts. In medicine, they are used to deliver medicine at a constant rate under the skin, helping to manage symptoms such as pain, nausea, and vomiting [9]. In laboratories, they are used to automate routine life science experiments that are taxing to perform by hand [10] or for microfluidics experiments where precise flow rate control is necessary [11]. Syringe Pump prices range between £300 and £2800 [12] for what appears to be a simple piece of equipment. Medical equipment businesses can charge a high price for 2 reasons:

- Cost of getting a medical device approved by regulatory boards such as the FDA and MHRA
- Lack of market competition

For laboratory work, this price point was too high to warrant buying many of them. To solve this problem, scientists have turned to open source hardware to build extensible Syringe Pumps tailored to the work being done

Back in 2014, a group from Michigan Tech University released the Open-Source Syringe Pump Library (OSSP). They provided a proof of concept for a 3D printed Syringe Pump that costs £70 that performs better than most commercial Syringe Pumps in terms of speed and force but is not as accurate as more expensive models [12]. The 3D printed files, bill of materials and build guide were made available for users to build and modify on Appropedia [13] and has been downloaded almost 9000 times [14]. The pump itself is a proof of concept, so members of the open source community have designed modifications to improve on the original design. One such project is the Lynch Pump Modifications that provide a new carriage and syringe holder that are vastly superior to the original designs [15].

There are 2 interesting papers that have built upon the OSSP for specialized use cases in laboratories: The Programmable Dual Syringe Pump (PDSP) and the Poseidon Syringe Pump and microscope.

The PDSP fuses together 2 OSSPs to automate laboratory work in life science applications. More specifically, infected blood cells are infused from one pump to another via a homogenizer. The homogenizer breaks down these cells into their liquid protein constituents with each infusion through it. This process is repeatedly done by hand and allows scientists to analyze the structure of blood cells. Doing this process by hand led to user-dependent variation in the results and damage to the equipment as pressure was applied unevenly [10]. Using the OSSP with a Raspberry Pi controller and a touchscreen interface, they designed a GUI in Python with Tkinter. This system is fully customizable for up to 16 pumps working concurrently and can be used in other areas of lab work.

The Poseidon Syringe Pump is a modified OSSP that incorporates a microscope to perform experiments on microfluidic devices where liquid is infused into systems as small as 10 microns wide [11]. These experiments require a flexible device that can provide precise flow rate control and allow the user to customize the operation software for their use case. Commercial syringe pumps are inadequate for this task since their software is closed source and limited. The pump itself is driven by an Arduino microcontroller that receives software calls from a Raspberry Pi with a touchscreen interface. The GUI is written in Python and uses the PyQt library.

Systems such as the 2 described show that there is a need for a cheap and customizable alternative to commercial syringe pumps. There exist some trivial projects that incorporate syringe pumps into robotic mechanisms such as the 8ARM Precision Pump. This mechatronics system acts as a robot bartender capable of mixing drinks to a high degree of accuracy, around 1 +- 0.05 cL. Although this is an interesting concept there are many environmental variables that the system cannot account for [16].

Open Source is a blanket term for many different criteria that can be applied to anything people can modify and share because its design is publicly accessible. These criteria include free redistribution, access to source code and allowance for modification and derivative works [17]. Use of the term open source began in software around 1990, where development shifted from large scale and rigid waterfall models to iterative development styles like Agile. This change brought about more democratic software development, with project such as Linux and GitHub being developed by hundreds of individuals who weren’t motivated by money, but by seeing what they could build together. This idea became a philosophy for many programmers and led to the creation of systems such as Arduino [18], Android [19] and Apache [20] which continue to grow to this day.

Economists would have you believe that innovation comes solely from competition within markets: businesses competing to gain the largest profits by creating the best product. This point is antithetical to the philosophy of open-source development [17]. Open-source still allows for businesses to profit from open-source work, depending on the license type a project falls under, but the driving factor is innovation first and foremost – innovation coming from any individual/party with an interest in the research. With the internet allowing information to spread faster than ever before, open-source has the means to fully democratise information and prove that Isaac Newton’s famous quote: “If I have seen further it is by standing on the shoulders of giants” is as true today as it was in his day. [21]

For the context of our project, we are going to look at Free and Open Source Hardware (FOSH). This has become a popular topic in the last decade, with 3D printing as a driving force to find cost-effective, reproducible solutions to expensive commercial equipment. Centralized repositories containing FOSH projects include the Open Source Repository [22], the NIH 3D Print Exchange [4] and journals such as HardwareX [23] and the Journal of Open Hardware [24]. A boundary to progress for FOSH projects comes from how it is licensed. There are 2 main classes of open source licenses:

- Copyleft – Users can redistribute the original work or any derivative work so long as it uses the same license as the original work
- Permissive – Users can redistribute the original work or any derivative work under any license they choose

Copyleft licenses preserve the original works license through any derivative work – that is work that modifies the original. On the other hand, Permissive licenses allow redistribution of work in any setting: open source or commercial. Permissive licenses allow for large scale implementation of derivative work since the project can be turned into a business while still preserving its open source roots. The best example of this is the Android operating system, allowing users to distribute applications under any license while the OS remains open source.

FOSH requires a self-sustaining community to provide new points of innovation and collaboration. We see this with websites such as Thingiverse – a huge repository of 3D printing projects and Just One Giant Lab (JOGL) – a place where volunteers can get involved in current open source projects. Individuals such as Linus Torvalds and Richard Stallman have been pivotal in the emergence of open source, and for FOSH one such individual is Joshua Pearce. He works at Michigan Tech and has worked in the FOSH community for over a decade. His work includes the Open Source Syringe Pump Library [12] and the RepRapable Recyclebot [25] – a system to turn household plastics into printable 3D filament. He has also written 2 books explaining open source to the layman through DIY projects and many articles explaining the benefits of adopting FOSH in scientific fields such as nanotechnology [26]. His research has been cited over 15,000 times and has inspired many derivative works such as this project. Without him the FOSH community and my own project would be very different.

3D Printing as we know it today began in 2005 at the University of Bath with the RepRap project. It intended to create a cheap 3D printer that could print its own parts, eventually becoming a self-replicating machine. Their first machine cost £430 to produce which then printed parts for the second machine, costing £300. In the first year and a half more than 2500 RepRap machines were built [27]. Before this, 3D printers would cost over £25,000 and used a technique known as Fused Deposition Modelling (FDM) whose patent wouldn’t expire until 2009 [28]. This patent, along with several others filed by Stratasys Inc, allowed the company to monopolize the 3D printing market, charging extortionate amounts for their products. The expiration of the FDM patent brought about a new age for 3D printing, with companies such as Ultimaker and Creality bring the cost of such printers down to as low as £200.

FDM is how the majority of modern 3D printers work: they deposit filaments of thermal plastics along a pre-defined path to create an object. The most used plastics are PLA, ABS and TPU, each with their own benefits and drawbacks. There are 2 configurations of 3D printer currently found on the market:

- Cartesian Printers
  - 3 axis system of rails and belts that can move the print head or print bed in the X, Y and Z direction one at a time
  - Movement paths are done one axis at a time using cartesian equations (x and y terms only)
  - Moving parts are heavy so print speed tends to be slower (around 60 – 80 mm/s)
  - Such printers include the Creality Ender printers and MakerBot’s Ultimaker printers
- Delta Printers
  - 3 independent arms on rails that move just the print head, the print bed is motionless
  - Movement paths are calculated using trigonometric functions between the arms for multi-axis movement
  - Circular print bed allows for a smaller form factor
  - Lighter print head, allowing for faster print speed (around 70 – 120 mm/s)
  - Example printers include the Anet A4 and the FLSUN Q5

To make use of a 3D printer, you need a 3D model file (usually as a ‘.stl’ or ‘.obj’) and some slicing software (such as Cura or PrusaSlicer). 3D models can be built yourself using a program like Blender or Fusion 360 or found on sites like Thingiverse that host thousands of models. The slicer will take your model file and printer configuration to generate a ‘.gcode’ file. This file is a list of hardware instructions telling your printer when to heat up, where to move and when to extrude plastic. Slicers contain a wealth of configurable settings to help calibrate your printer – a process required on most new printers.

With the 3D printing market valued at £9.7 billion in 2020 with an average growth rate of 14.6% annually [29], the future impact of this technology on the environment must be considered. Waste plastics currently account for 5 million tons of waste every year in the UK alone [30] and a new wave of plastic manufacturing could add to that. Fortunately, one of the most used 3D printing plastics, PLA, is biologically sourced from fermented corn and can biodegrade in industrial composting procedures. These conditions require a constant temperature of 40-50 degrees for between 47 to 90 days, at which point PLA breaks down into water and carbon dioxide [31].

There are also upcycling initiatives in the 3D printing community using RepRap Recyclebots [25]. These devices allow users to take household plastics such as milk, water and detergent bottles, shred them and extrude them into usable 3D printer filament with a diameter margin of error of <5%. This brings the cost of 1kg of filament from £20 to less than 2p. The device itself costs around £540 to make, with the return on investment being a big adoption factor.

The future of 3D printing hinges on the community of makers working together to show the benefits of this technology to consumers. Thingiverse was created in 2008 alongside the RepRap project so users could make and share designs, and currently hosts over 2 million models. The website Reddit has several friendly communities dedicated to 3D printing such as r/fixmyprint, r/functionalprint and r/3dprinting along with communities for all common brands of printer. Having bought an Ender 5 Pro for this project, the maker community has been an excellent resource for learning what these machines can do.

When medical syringe pumps were first adopted in the 1980’s, there was a single company who manufactured and distributed them – Graseby Medical. [32] Other companies attempted to enter the market such as Baxter International, but never gained wide adoption since Graseby beat them to market. Problems then arose in 1994 when hazard notices from the British Medical Devices Association (MDA) came out regarding the confusion of 2 Graseby pump models [33]. The MS16 model infused at millimeters per hour, whereas the MS26 infused at millimeters per 24 hours. The similarity in design meant medical staff would occasionally confuse the 2 pumps, leading to a rise in inappropriate infusion rate errors and patient deaths. The MDA’s notices required users to use ‘enhanced labelling’ to ensure the 2 types of pump were not confused. At the time, few alternatives existed on the market and the cost of new equipment and retraining staff was too high.

These notices did very little to mitigate the initial problem, and in 2010 a report from the National Patient Safety Agency (NPSA) explained the need to remove these problematic systems from use [33]. It reported that between 1st January 2005 and 30th June 2010 there were 175 incidents involving Graesby syringe pumps, 8 of which resulted in patient deaths. These incidents were caused by ‘incorrect rate setting’ due to human error and ‘unexplained fast infusion’ caused by device failure. This report highlighted the need for new equipment and better staff training: a need that had been ignored over 15 years prior.

Following this report, a transition plan was put in place for the next 5 years. This would involve slowly phasing out Graesby syringe pumps and retraining staff on new equipment from McKinley Medical that infused in mL per hour. This process had to be a balance between the cost of replacement programs and increments in patient safety afforded by new technology. Phasing out the older syringe pumps had to be slow to ensure patients who required the equipment were able to continue their treatment. The NHS Purchasing and Supply Agency knew this back in December 2008 but were unwilling to make the change, stating: “currently there are safer alternatives to the MS26/MS16 pumps on the UK market… adopting safer syringe drivers would require modification of established working protocols and practices in UK palliative care, and a significant amount of retraining for staff”. This lack of action led to 4 deaths in 2009 caused by incorrect use of the Graesby pumps.

A report in November 2018 from the Department of Health and Social Care reviewed the action taken following the NPSAs 2010 report [34]. It showed that action had slowed by 2013, with a further NPSA report reinforcing the need to switch from Graesby pumps by 2015. They reported a further 23 incidents of harm involving these pumps between 2011 and 2012, although none were fatal. Reports from the media eventually led to the full removal of these pumps from use.

In hindsight we can see that the NPSA were aware of the problem for 15 years before action was properly taken, the process of adopting new equipment was one they were unwilling to make at the time. This was due to several reasons: lack of market competition, cost of equipment and retraining, balancing the use of potentially dangerous equipment with its ability to save lives. They also believed the initial problem could be fixed by solving the human error, a solution that didn’t work. This shows us that giving greater control to the hardware and minimizing human interaction could be a safer alternative, although it puts the manufacturer at greater risk when problems arise.

From this we can predict how an open source medical syringe pump could be implemented for use across the world and the important factors to consider: routine assessment of device safety, transition plan for both phasing the device in and out, constant analysis of the devices obsolescence. These are all iterative processes, plans that will change over time, and are suited to an open source approach. The real issue with bringing open source systems into the medical industry is regulation – how can we ensure consistent device quality when we aren’t manufacturing each device ourselves. One such solution is found with the charity Glia [35]. They have designed and built open source medical equipment such as stethoscopes and tourniquets, with their stethoscope becoming the first open source medical device to be clinically validated and widely available [36]. The work they’re doing shows that open source alternatives to medical equipment are viable and that over time, an open source approach to medical equipment and regulation could lead to safer equipment use.

This covers the series of files stored on the Gitlab repository for this project. The repository contains the files and build guides for both versions of the Syringe Pump, pictures, and schematics of the electronics setup along with documentation for the Pump operation code, GUI and Android application.

This documentation is for users who wish to replicate and build upon the current state of the Pumpy Syringe Pump project without delving too deep into the academic side of the project.

Below I describe the table of contents for the technical documentation along with the link to it in the repository:

https://cseegit.essex.ac.uk/ce301_2020/ce301_woolsey_daniel.git

TABLE OF CONTENTS

1. Syringe Pump v1
  a. Build Guide
  b. Modifications
2. Syringe Pump v2
  a. Build Guide
3. Electronics
4. Testing Suite
  a. Pump Operation Calculations
5. Pump UI
  a. Kivy GUI
  b. PyQt GUI
6. Android Application
  a. Pumpy App
  b. Bluetooth Handler
7. Documents

This project is primarily hardware focused and choices have had to be made to pick the correct equipment. Below I describe the electronics and syringe pump hardware chosen for this project: their specifications and the reasoning behind choosing them.

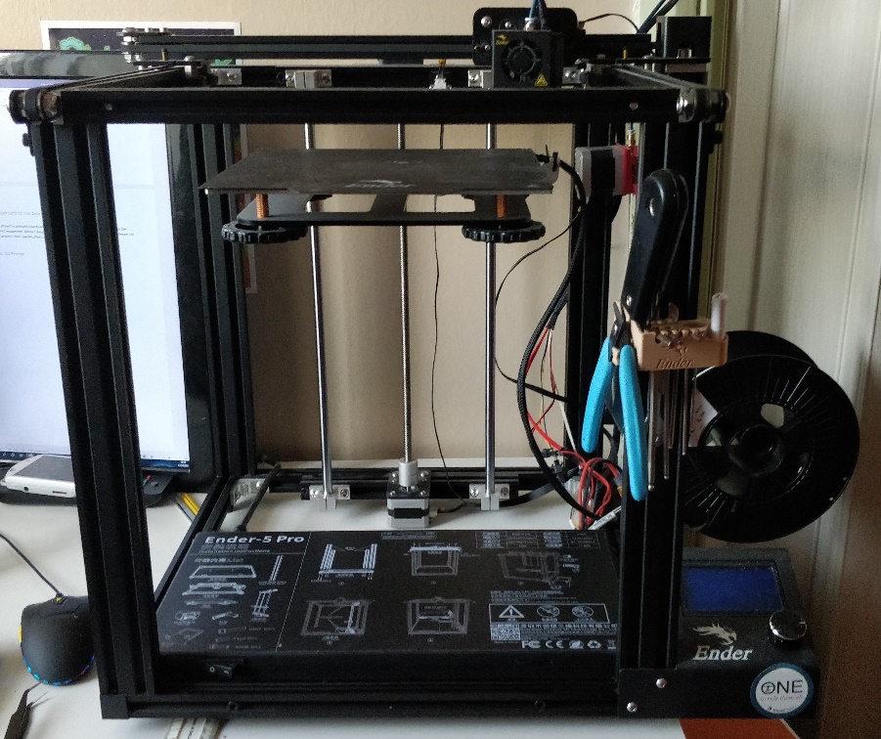
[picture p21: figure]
Ender 5 Pro 3D Printer

For a 3D Printer I went with the Creality Ender 5 Pro: a cartesian gantry consumer grade printer. It makes use of FDM (Fused Deposition Modelling) to extrude a variety of plastics onto the heated bed. This printer retails at a cost of £294.64 from the manufacturer but can be found cheaper at other online vendors [37].

I chose this printer over other similar models for several reasons:

- Upgraded motherboard for a quiet and more precise printing performance
- Large build plate (220x220x300mm) for printing bigger models
- Bowden tubing to accommodate printing different plastics such as flexible filament

All the parts for both syringe pumps are printed using 1.75mm diameter PLA filament from 3DJake and Geeetech. I chose PLA due to its wide availability, tensile strength, and biodegradability [27]. The cost for 1kg of generic brand PLA is between £19 and £25 from Amazon.

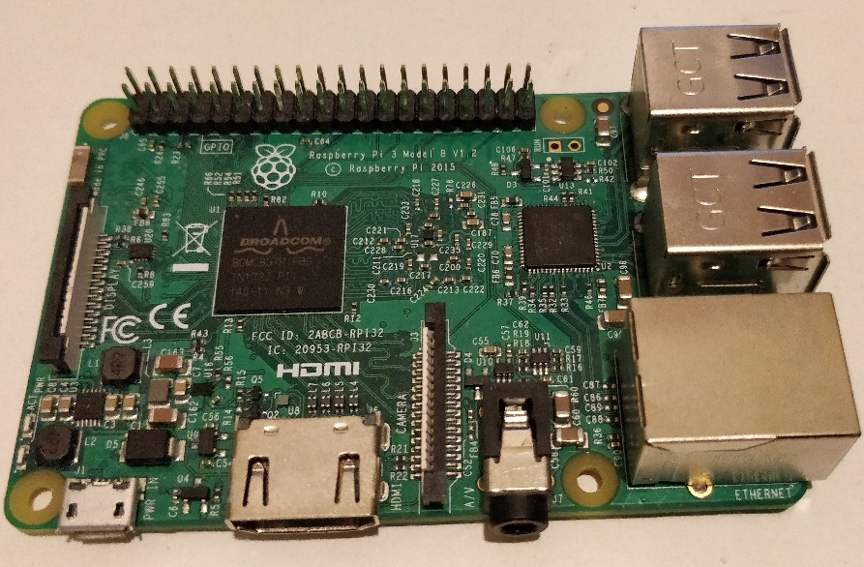
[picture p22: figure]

The microcontroller is the most important component of this project: it handles all aspects of pump operation and control. Commercial pumps make use of bespoke embedded software chips from companies such as CME Medical. Other Open Source pumps make use of 3D printer driver boards such as RAMPS or Arduino [11]. The biggest issue with these is their minimal operating systems that provide the bare minimum of utilities for a developer.

With that in mind I had to decide on a microcontroller that fit the specifications of my project:

- Handles touchscreen display for easy user interaction
- Large amount of digital I/O for required peripherals and extensibility
- OS that can run a programming language with libraries for a GUI
- Communication with mobile devices either by WiFi or Bluetooth
- IoT (Internet of Things) compliant for future updates

The Raspberry Pi fits all my requirements for a microcontroller: it runs a flavor of Linux called Raspbian with great developer support, 40 GPIO (general purpose input/output) pins for external peripherals, HDMI output for a video display, WiFi and Bluetooth built in for communication and external updates.

For a microcontroller this is an expensive option at £35 from eBay, whereas an Arduino based microcontroller (Arduino Uno) costs around £5 from eBay. The extra features and Linux-based OS we get from the Raspberry Pi makes it much easier to build the software we want.

# 4c. NEMA 17 Motor

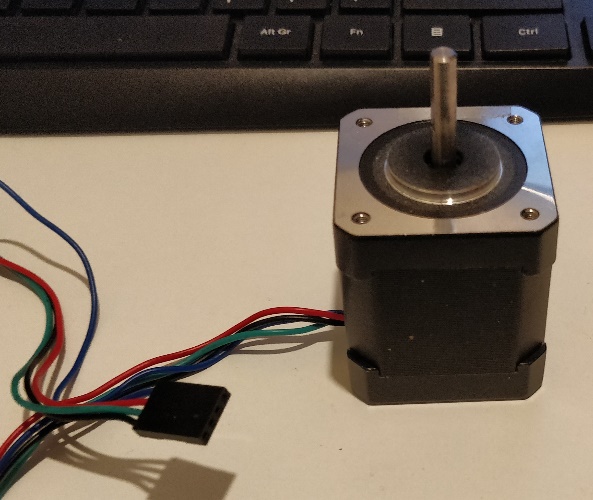
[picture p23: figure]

Stepper motors can be bought with various specifications: voltages up to 24V, current between 0.2A and 2A, and face plate sizes from 0.8 inches up to 4.2 inches. Previous open source pumps have made use of both NEMA 11 and NEMA 17 motors [12] and I chose to use a NEMA 17 (17 meaning a 1.7-inch faceplate). They are commonly found in 3D printers and CNC machines and require a motor driver for the Raspberry Pi to run them.

The version I chose runs on 12V at 2A and can handle up to 24V but that isn’t necessary for our application – pushing a syringe with liquid inside doesn’t require a force that large and would create unnecessary vibrations during operation.

Smaller versions of the motor could be used to reduce the build size if a user wanted but would involve modifying the current 3D printed files that are designed with a NEMA 17 motor in mind.

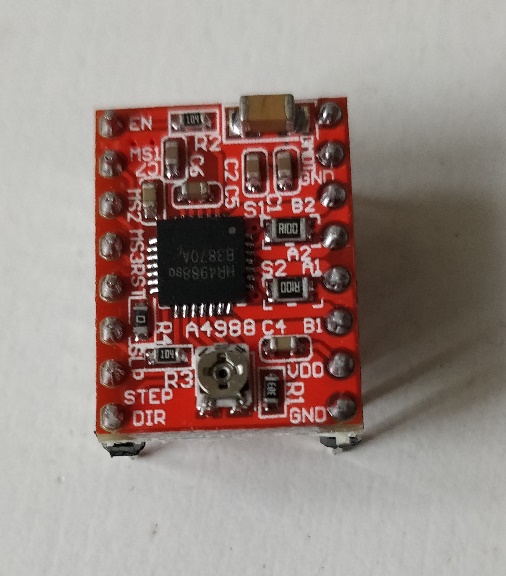
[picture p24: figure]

The A4988 is the most used driver for stepper motors and can be found in most 3D printers. Its prevalence means it’s cheaply available at roughly £3 from eBay. I could have gone with a DRV8825 motor driver which is built to handle higher voltage and current, but the NEMA 17 motor I’m using can handle 24V at 2A which is well within the tolerance of the A4988. This also has a current limiting potentiometer on the board which is used to prevent damage being done to the motor by the power supply. Since our power supply matches the specification of the motor, we don’t need to worry about adjusting it.

It also has 5 micro-stepping modes ranging from 200 steps per revolution up to 3200. There is negligible difference in positional accuracy of the stepper motor as we increase our steps per revolution, but we do benefit from reduced vibration [38]. For our Syringe Pump it is likely to be operating for up to 24 hours continuously, so a greater number of steps per revolution can provide smaller dosages more regularly for greater control of liquid infused.


When choosing a touchscreen display for the Raspberry Pi I had to decide on the best input method from the following options:

- Ribbon cable directly inserted into the Raspberry Pi
- GPIO and HDMI inserted into the board
- USB and HDMI inserted into the board

The first option can only be found on touchscreens built by the original Raspberry Pi manufacturers – these are expensive at £60 from The Pi Hut and you can get the same performance from a 3rd party touchscreen for £30 to £40, albeit without the ribbon cable interface.

The second option can be seen on the left-hand side image above, an Elecrow 5-inch TFT Display (£40). This requires 26 GPIO pins and an HDMI connector which is unhelpful for our build. It uses all the 5V power pins on the board so I had to solder a jumper cable to power the motor driver and other components – if done incorrectly this could damage the display. The screen also sits above the rest of the GPIO pins making it awkward to setup other I/O and as such I chose a different display.

Finally, I found the 3rd option seen on the right-hand side in the image above. This is a Waveshare LCD B and costs around £43 from Amazon. It interfaces with the Raspberry Pi using USB and HDMI, leaving the GPIO available for any extra peripherals we may want to use. Since we need space for a breakout board to attach our motor driver to, this display was the best option.

The Waveshare LCD comes with a CNC cut case and I have provided 3D printed files for attachable legs as a case stand. The touchscreen works right away with the Raspberry Pi and can be calibrated easily in the settings menu.


This first iteration of the Syringe Pump is a modified version of the Open Source Syringe Pump [12]. The main printed sections of the pump are as follows:

- Motor End – Holds the motor and steel rods together
- Carriage – Contains the linear bearings and plunger holder, moves along the rails and threaded rod
- Plunger Holder – Made up of 2 parts, the Body Holder attaches to the carriage for the plunger to slide into and the tab stops the plunger from moving
- Idler End – Holds the steel rods and ball bearing to the Syringe Holders
- Syringe Holders – 2 of these are attached to the Idler End with space between to insert and tighten the syringe body

The biggest issue I found with this design is the replacement of a syringe using the Syringe Holders. They require you to loosen the screws on the Idler End to remove it and then retighten the screws after. This issue is dealt with in the next iteration of the pump.

The last important piece of the pump is the threaded rod coupled to the motor that runs through the carriage. This allows the carriage to run up and down the pump when the motor is activated. The pitch (distance between 2 threads) of the rod is essential to calculating the distance travelled when the motor moves the coupler. The diameter of the rod is linked to the stability of the pump: the greater the diameter of the rod the less the pump will vibrate. This model uses a 5mm diameter rod, something I’ve chosen to upgrade for v2.

The image above of the Syringe Pump v2 is similar in design to the v1 pump, with some modifications based on issues with v1 and from another Syringe Pump project [39]:

- Carriage – Redesigned with hand knobs for easy syringe replacement and space underneath for limit switches to prevent over-infusion and damage to both the Carriage and Idler End
- Limit Stoppers – 2 of these are placed on one of the steel rods during assembly and can be moved by loosening the hand knobs on the side for setting up different sized syringes
- Syringe and Plunger Holders – Both use a similar design, also incorporating hand knobs, to allow for easy syringe replacement
- Coupler – I replaced the metal coupler with a 3D printed one since it was tighter, stronger, and cheaper

For the threaded rod, I raised the diameter from 5mm to 8mm which helped deal with the vibration issues I had with v1. Choosing a different sized threaded rod meant that I had to redo my calculations for distance travelled by the carriage – both versions of these calculations can be found in Section 5c.

The hand knobs are designed such that no screwdriver is needed when replacing the syringe. Occasionally the bolts can come loose from the hand knobs so using super glue on the hand knobs is advised. In the future I plan to adjust their design so that this is no longer an issue.

Having chosen the hardware and built both versions of the Syringe Pump, I had to decide on the appropriate software tools. This involved testing libraries, building user interfaces, and designing a mobile application.

Since I had picked the Raspberry Pi as my microcontroller I was able to develop my software on Raspbian, a flavor of Linux. This gave me a wide variety of languages and libraries to choose from when developing each aspect of the software.

For hardware level programming, the Raspberry Pi gives us libraries [40] for 4 languages: C, C++, Python and Processing3. The choice of language here will persist over almost all aspects of development so I had to choose something I was both comfortable with and could build GUIs with easily.

Processing3 is more of a teaching tool and IDE built on top of other languages, with variants existing for Java, JavaScript, and Python [41]. It allows beginner programmers to work on basic frontend projects before exploring other languages. Building a GUI with Processing3 could be easy, but I was unfamiliar with the language and libraries it provided.

C and C++ both interact with the Raspberry Pi using the same set of libraries – either libgpiod or pigpio. As they are both compiled languages, they can provide a more sophisticated development experience, with speed and efficiency greater than scripting languages such as Python. I have a small amount of experience with both these languages and knew that building a GUI along with a Bluetooth handler could lead to development issues that would halt the progress of the project. As such, I decided to go with the last option – Python.

According to the PYPL (PopularitY of Programming Languages) the most popular language used for tutorials via Google Trends is Python [42]. It’s a widely used language with many libraries for all aspects of development. This helps massively with combining the hardware code with GUI code as well as implementing remote control via Bluetooth. For these reasons, along with my own history with Python, I chose this for my language.

To get our motor driver working we must use Pythons `RPi.GPIO` library. This library allows us to initialize the GPIO pins we’re working with:

- DIR – Pin 20 – Tells the motor which direction to move in (clockwise/anti-clockwise)
- STEP – Pin 21 – Tells the motor to move a single step
- MODE – Pins 5,6,13 – Tells the motor what level of micro-stepping we want

For setting up our MODE output, we have a dictionary mapping the micro-stepping level to a tuple containing the appropriate configuration.

From here we can make the motor do a full revolution at any given micro-stepping mode. We do this by setting our DIR pin to clockwise (integer value 1) and MODE pins to the appropriate dictionary entry. Then we iterate through the number of steps per revolution our MODE is set to, activating the STEP pin, delaying for a short time, then deactivating the STEP pin. We require a delay between STEP pin writes to compensate for our code working faster than the motor can handle. For testing purposes, we delay for 0.005s but for our Syringe Pump we will calculate this delay based on how long the user wishes to use the Pump for.

Now that our Pump can move forwards and backwards, we must write some code to allow it to act as a Syringe Pump should. This means we must take some information from the user about the syringe and how long the infusion will take – then ensure the Pump infuses the full syringe in the given time frame.

To make this as easy as possible, we will generate 2 lookup tables – one for each Pump version – that can tell us how many steps (at a given micro-stepping value) it will take to fully infuse a specific size syringe.

To do this we have to calculate 3 values:

- Travel (mm) – Distance the carriage has moved along the threaded rod
- Conversion Ratio (mL/mm) – This will convert the travel distance in mm to the volume of liquid infused in mL
- Volume Ejected (mL) – The total volume of liquid infused by the Pump

TRAVEL

Travel (T)=pitch* (steps taken)/(steps per revolution)

Pitch is the distance between 2 threads on a threaded rod

For Syringe Pump v1, our pitch is 0.8mm and for Syringe Pump v2 it’s 2mm.

CONVERSION RATIO

Conversion Ratio (CR)= (volume of syringe)/(length of syringe)

The length of the syringe may vary between brands, so these calculations are configured to the BD Plastipak brand of syringes. Most commercial Syringe Pumps will require either a specific brand of syringe or will allow the user to choose which brand they have and will configure themselves accordingly.

Our system is configured for 20mL and 60mL BD Plastipak syringes which are of length 70mm and 109mm respectively.

VOLUME EJECTED

Volume Ejected (V)=((volume of syringe)/(length of syringe))*(pitch* (steps taken)/(steps per revolution))

V = CR * T

This formula allows us to calculate the volume of liquid infused by the Syringe Pump based on the syringe itself and the steps the motor has taken. From this we can calculate the number of steps taken to infuse a full syringe at a given micro-stepping rate.

For each micro-stepping rate, we double the steps per revolution value, so these values will be 200, 400, 800, 1600 and 3200.


Doing this for both pumps and each micro-stepping value, I had the values for my lookup tables shown below.

With the code written for basic pump operation and lookup tables for syringe infusion calculated, it was time to bring them together. The lookup tables are implemented as dictionaries mapping syringe size values to a dictionary of micro-stepping values to their respective step counts. These tables are calculated manually for now, although I would like to add a software component that allows users to add custom syringes that are selectable in the main GUI.

Next, I had to use these lookup table values to calculate the required delay between motor steps. For consistency I decided to keep all time variables to seconds, including the user input time. In the future I would allow for user to select a unit of time, either seconds, minutes or hours, and the code would perform the conversion to seconds if required. Then we can divide the users time input by the total number of steps from the lookup table to get the delay per step.

Our previous pump operation example uses 2 delay calls: one after activating the STEP pin and one after deactivation. This means we divide our delay value by 2 to get our actual delay between pin writes. Combining these steps together we can write functions to infuse a full syringe.

To finish up the testing suite, I implemented functionality for continuous withdrawal and infusion at a user defined micro-stepping rate. The delay for these functions is hardcoded into a dictionary that divides the initial delay value (0.005s) by 2 for each level of micro-stepping. This way no matter what the micro-stepping value is the continuous operations will always take the same amount of time. This is better shown in bullet points:

- MS Value – 1 – Delay = 0.005
- MS Value – 1/2 - Delay = 0.005/2
- MS Value – 1/4 - Delay = 0.005/4
- MS Value – 1/8 – Delay = 0.005/8
- MS Value – 1/16 – Delay = 0.005/16

The full documentation for the testing suite can be found in the GitLab documentation outlined in Section 3.

With all the functionality tested and working correctly, I had to properly encapsulate this data into a class. Doing this improves the readability of the code and allows us to import the functionality into any other Python file. Since I planned to build a GUI and Bluetooth handler, keeping operation functionality in its own class was the best way to implement the system.

This class, known as Pumpy, involved having pin values be customizable in the constructor in case of future electronics updates, creating a pump method that combined together all the elements from my testing suite, implementing a continuous operation mode and bringing in limit switch support for the Syringe Pump v2. These act as while conditions for both continuous and pump operations, ensuring the pump stops if the appropriate switch is pressed.

With all the pump operation handled, it was time to decide on an appropriate GUI library. Pythons popularity means that a large number of well documented libraries exist for building GUIs, including Tkinter, PyQT and Kivy. These libraries can all register touchscreen input as a mouse event, meaning no extra work was needed to make the GUI touchscreen capable.

Tkinter was the first library I looked at since it’s built directly into the Python standard library. Several great tutorials exist to walk the user through since most Python users will try Tkinter as their first GUI library, so I tried the Coders Legacy tutorial series [43]. Designing a GUI is done programmatically, so elements are either managed by a preset layout that determines their location on screen or the user hardcodes their locations in a fixed window size. Both methods were unsuitable for my initial GUI design, so I looked for another library.

Kivy was the next library I tried since it has a different method for designing GUIs. This involves using a separate ‘.kv’ file to define the structure of your GUI which can be imported into Python to add functionality. The pong game tutorial on the Kivy website gives a great introduction to the Kv file syntax and building a functional GUI [44]. Once I began working on my own GUI, I encountered the same issues I found with Tkiner: properly formatting layouts to display elements where I wanted them was a challenge. I decided to switch libraries again to one that allowed me to design my GUI with external software.


This is where I began working with PyQt5. A program called Qt Designer is installed alongside the PyQt library and allows us to build a GUI in a much more intuitive manner. Once your design is completed you can export it as a ‘.ui’ file which can be imported into Python. There you can implement your functionality using the PyQt5 library. This was a much better way of building a GUI and is how I decided to build my application.

With a GUI in place I had to decide how I would operate the system remotely. This required picking a mobile platform and a communication protocol to send data over.

For a mobile platform I had 2 choices: iOS or Android. As of March 2021, Android is present on over 70% of mobile devices with iOS trailing at 27% [45]. On top of this, iOS charge $99 a year as a developer fee to access advanced tools and upload your application to the App Store [46]. All of this, along with the fact that Android began as an open source project, pushed me to develop my application on Android.

Developing for a new platform meant working with a new programming language. Android applications can be written in one of 2 languages: Java and Kotlin. Kotlin is a variant of Java meant to make development easier and is used primarily for Android development. Learning Kotlin for building this application could prove to be time consuming, and since I have used Java throughout my degree I decided to work with Java.


Google provide the Android Studio IDE for free which contains tools for designing an interface, incorporating external libraries, and testing the application with an Android Emulator. By activating developer mode on an Android device, you can also upload your application directly to the device for further testing.

Android also has libraries for directly interfacing with a devices Bluetooth adapter. This meant I could search for and connect to external devices over Bluetooth for transmitting and receiving data. Since the Raspberry Pi has built in Bluetooth, I could build a Bluetooth handler using Pythons ‘pybluez’ library to accept a connection from the mobile application. From here I can wait to receive operation information or send information back to the mobile application.

Bringing all these features together gives us the Pumpy software pipeline: hardware operation, touchscreen GUI and mobile application.

Here I will go through the steps I took to bring together the hardware and software elements from Sections 4 and 5 into my final product.


Once I had my 3D printer built and setup, I had to choose some slicer software. This allows the user to import 3D models, tune various printer settings and generate a ‘.gcode’ file that the printer can run. For this I chose Ultimaker Cura: it’s the most popular slicer since it’s free, open source and has many advanced settings.

With the software in place, I had to adjust some settings to ensure my prints were of a high quality:

- Initial Layer Height – This ensures the first layer printed adheres to the print bed, this is important because if the first layer fails then the rest of the print will warp as a result. Making the initial layer height shorter than the normal layer height allows the plastic to squish flatter against the print bed. Based on the printers design, there are so called ‘magic numbers’ that work best for layer height. For my printer these are increments of 0.04mm, so I use 0.08 and 0.12mm as my layer heights.
- Print Speed – Since I’m using a cartesian printer I ensure consistent quality prints by using a speed between 60 and 80mm/s. Going higher than 80mm/s creates gaps in the print layers since the printer extrudes plastic slower than the print head moves.
- Retraction – There are 2 main retraction settings: Speed and Distance. When the print head must move over a gap without extruding it performs a retraction: the filament is pulled a given distance out of the nozzle at a given speed. This is used to avoid stringing, where filament still in the nozzle is pulled along the print creating thin and unwanted lines over gaps. An example image is provided to the right.

Having completed several test prints such as the retraction tower shown above, I got to work printing the 3D parts for the Syringe Pump v1.

The original design of my pump makes use of the files provided in the Open-Source Syringe Pump Library [12]. My aim was to build and test this design, noting modifications I wanted to make as I went along. Using these, I could improve on an initial working design before adding my own features to the pump.

Both pump versions use a similar set of parts that cannot be 3D printed. The 2 most important parts are the threaded rod and the motor. The specifications of the threaded rod and motor will dictate how I calculate the infusion operation as well as the sizes of all the 3D printed parts.

Below are both of the bill of materials tables for each version of the Syringe Pump along with the total cost (not including 3D printed parts):


SYRINGE PUMP v1

SYRINGE PUMP v2

The majority of the materials were sourced from various UK based eBay sellers between 2020 and 2021, so prices could change, or other vendors may offer a cheaper alternative.


For the Syringe Pump v1 we make use of the following 3D printed parts which are shown in the image below from left to right:

- Motor End
- Carriage – Modified
- Plunger Holder Base
- Plunger Holder Tab
- Idler End
- Syringe Body Holder (x2) - Modified

The total print time for all these parts was 17h2m and used up 82 grams of PLA filament.

The modifications made to the Carriage and Syringe Body Holders was done using Autodesk Meshmixer. This software allows users to import model files in the ‘.stl’ or ‘.obj’ format and modify them however they choose.

For the Syringe Pump v2 we use the following 3D printed parts, shown in the image below from left to right:


- Back Support
- Coupling
- Carriage
- Limit Stop (x2)
- Front Support
- Wire Holder
- Plunger Holders
- Side Syringe Holder
- Slider
- 7mm Hand Knobs
- 8mm Hand Knobs
- 9mm Hand Knobs

The total print time for all these parts was 16h58m and used up 79 grams of PLA filament.

All the model files in ‘.stl’ format can be found in the GitLab repository provided in Section 3.

Here I will discuss the process I went through building the Syringe Pump v1, the modifications I chose to make and the process for building the Syringe Pump v2.

With all the 3D printed parts completed and the bill of materials ordered it was time to build. The Open Source Syringe Pump Library has a build guide on its Appropedia page [13] which was simple enough to follow but had some difficult steps. The carriage model they designed required you to cut holes for the linear bearings to be inserted. Instantly I realized how difficult this was in practice and made a note of it for modification.

When sliding the carriage onto the 3 rods I realized how loose it was without a syringe and the Plunger Holder Tab inserted. To compensate for this, I decided I would have to get rid of the small nut underneath the carriage that the threaded rod goes through and replace it with a more stable part such as a lead screw nut.

The Syringe Body holders were designed for use with 20mL syringes only: the top of the holder was a closed circle. For my project, I had discovered that medical syringe pumps make use of 20mL and 60mL syringes. This meant I had to either modify these or design new ones from scratch.

Once it was fully built, I wired up the motor to the A4988 motor driver, connected that to the Raspberry Pi and wrote the first part of my testing suite. Here I discovered that when calibrated at the micro-stepping values ‘1’ and ‘1/2’ the motor would vibrate strongly and slowly move across the table if left long enough. When tested at the 3 other micro-stepping values the effect was less noticeable. To deal with this I would have to either build a case to stop the pump from moving or increase the diameter of the rods to make the pump heavier and more stable.

Since I had a working syringe pump prototype, I was able to implement my infusion calculations described in Section 5c and ensure they functioned as expected.

From here I began to outline the modifications I wanted to make for a new iteration of the Syringe Pump.

With a better understanding of how the Open Source Syringe Pump Library worked, I collated together my modification ideas along with one from the Lynch Open Source Syringe Pump modifications page on Appropedia [15]. These modifications are listed below:

- Carriage
  - Add spacing to the underside of the carriage where the linear bearings are inserted to avoid users having to cut a space open themselves
  - Add spacing through the bottom where the threaded rod slides through for the same reason as above
  - Replace the M5 hex nut that holds the threaded rod in place with an attachable lead screw nut to help prevent unloaded carriage movement
  - Inclusion of limit switches to prevent the carriage pushing against the motor and idler ends which can damage them
- Plunger Holder Body and Tab
  - Widen both to allow for 60mL syringes, but would require modifying the carriage to accommodate the larger body
  - Design a new system that incorporates this into the carriage without a top so any size syringe will fit
- Body Holders
  - Use the Lynch modified body holders that remove the top section and allow for easy syringe removal – but these still don’t fit 60mL syringes
  - Use a single piece that pushes the body from underneath onto the idler end and tightens from the other side, ensuring any size syringe will fit and only requiring 2 screws to tighten
- Steel and Threaded Rods
  - Make all these thicker to help reduce vibration from the motor, would require modification to both ends and the carriage

These modifications led me to look at various syringe pump projects that people had uploaded to Thingiverse. Here I came across a design that incorporated many of the modifications I outlined above: limit switches on the carriage, improved syringe body and plunger holders and hand knobs for easy adjustment [39]. Using the OSSP as my template, I began incorporating elements of Andrey Samokhins design, along with my own ideas listed above, into the Syringe Pump v2.

While testing out modifications on my Syringe Pump v1, I wrote up a new build guide that includes my modified files which can all be found in the Gitlab repository from Section 3.

Once I had all my modified 3D printed files printed and ready, I put together and ordered the new bill of materials. This included 8mm rods instead of 5mm, a new touchscreen for a better electronics form factor, limit switches and a lead screw nut. The limit switches arrived attached to a breakout board that was too large for the carriage. This meant de-soldering the limit switch component from the board, which can be done with a soldering iron, solder and some tweezers.

During the build I noticed some issues with the hand knobs. The hex nut spacing inside of them was too large so the hand knob would slide away when in use. As a quick fix the user could superglue the hex nuts into the hand knobs, but I decided I would modify each hand knob size so the nut wouldn’t slip out.

The new design also used moveable limit switch stoppers for the left side steel rod. These would activate the limit switches attached to the carriage and tell the pump to stop moving. Since they could move different sized syringes could make use of them, but the user would have to set them up before filling the syringe. To get around this I made markings on the rod to identify where the limit stopper should be placed for 20mL and 60mL syringes. At this point I am still trying to decide on a better way to deal with this issue.

As I built this new version, I wrote a build guide which is available on the Gitlab repository found in Section 3.

With everything put together I modified my electronics setup to incorporate the 2 limit switches. After I ran my testing suite to ensure the carriage moved properly, I reworked my infusion calculations outlined in Section 5c to compensate for the wider pitch of the new threaded rod. With the new lookup table, I was able to test a full infusion and continuous activation using the limit switches. Here I also tested my 60mL syringe which fit comfortably into the new holders and ensured my lookup table was in working order.

Now I had a more appropriate pump for my project, I began work on cleaning up the electronics.

Before building each version of the Syringe Pump, I designed the electronics systems using Fritzing – an open source tool for building electronics designs. Below are both designs for the electronics systems:


ELECTRONICS DIAGRAM V1 ELECTRONICS DIAGRAM V2


Using these as a guide, I wired up a breadboard and tested each version of the pump. For Syringe Pump v1 I made use of a 3D printed case for the Raspberry Pi and touchscreen, attaching the breadboard to the back. The files for this case were created by bredita and uploaded to Thingiverse [47]. For Syringe Pump v2, a CNC cut screen housing was included with the touchscreen and I 3D printed legs created by Grey3000 on Thingiverse [48] so the enclosure could stand. Images of these breadboards and cases are shown below:


BREADBOARD V1

BREADBOARD V2

Once the breadboard systems were functional, I ordered a Raspberry Pi breakout board to replace the breadboard and soldered the components and headers onto it. This made setting up the pump a lot easier: insert the motor and limit switches into their headers, plug in the 12V and 5V power supplies and the system boots up. Below are images of the populated breakout board:


The next step was to work on a GUI to operate the device. As outlined in Section 5f I designed interfaces for 2 different libraries: Kivy and PyQt5. The features my GUI required were:

- Touchscreen friendly, no keyboard or mouse required
- Choice of syringe size and micro-stepping value
- Ability to continuously withdraw and infuse for setting up a syringe
- Stores and loads previous operations

As I worked with each library, I attempted to make the GUI comfortable to look at with a minimal set of visible features. This way new users wouldn’t be overwhelmed by complicated features on startup.


Working with Kivys layout system made it difficult to resize elements on the screen. This meant labels, buttons and input boxes would fill entire grids and appeared ugly when displayed. There is also no CSS support to create a theme, choose fonts and change colours – instead this is handled on an element by element basis which can be tedious.

For numerical inputs I had planned to implement a virtual keyboard that would pop up when the user clicked on the ‘Syringe Size’ or ‘Infusion Time’ input boxes. This feature would work on a lone application, but when testing it with my GUI I couldn’t get it to display consistently. When it did show up the keyboard suffered from input latency and didn’t feel comfortable to use.

For these reasons I chose to switch libraries to PyQt5.


Upon first installing PyQt 5, it also installed the Qt Designer – an application for building GUIs graphically rather than programmatically. The GUI designed is exported as a ‘.ui’ file that can be imported into Python to add functionality. This software gave me more control over each element’s location on the screen, its size, and its theme. Each element uses CSS to style itself, allowing users to design each element however they want.
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

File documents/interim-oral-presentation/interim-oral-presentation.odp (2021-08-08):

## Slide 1

Design and Manufacture of a Syringe Pump

Daniel Woolsey

Supervisor: Dr Nick Zakhleniuk

2nd Assessor: Dr Vishwanathan Mohan

## Contents

- Project Goals and Objectives
- Current Progress
- Project Planning (Agile/Jira)
- Project Management
- Future Work
- Conclusions


## Project Goals and Objectives

- Need for low cost syringe pumps; motivation
- Print and build a Syringe Pump
- Design and implement modifications to improve operation and usability in a medical context
- Incorporate a touchscreen interface as the primary method of control
- Build an Android application that can monitor and control the pump over Bluetooth
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

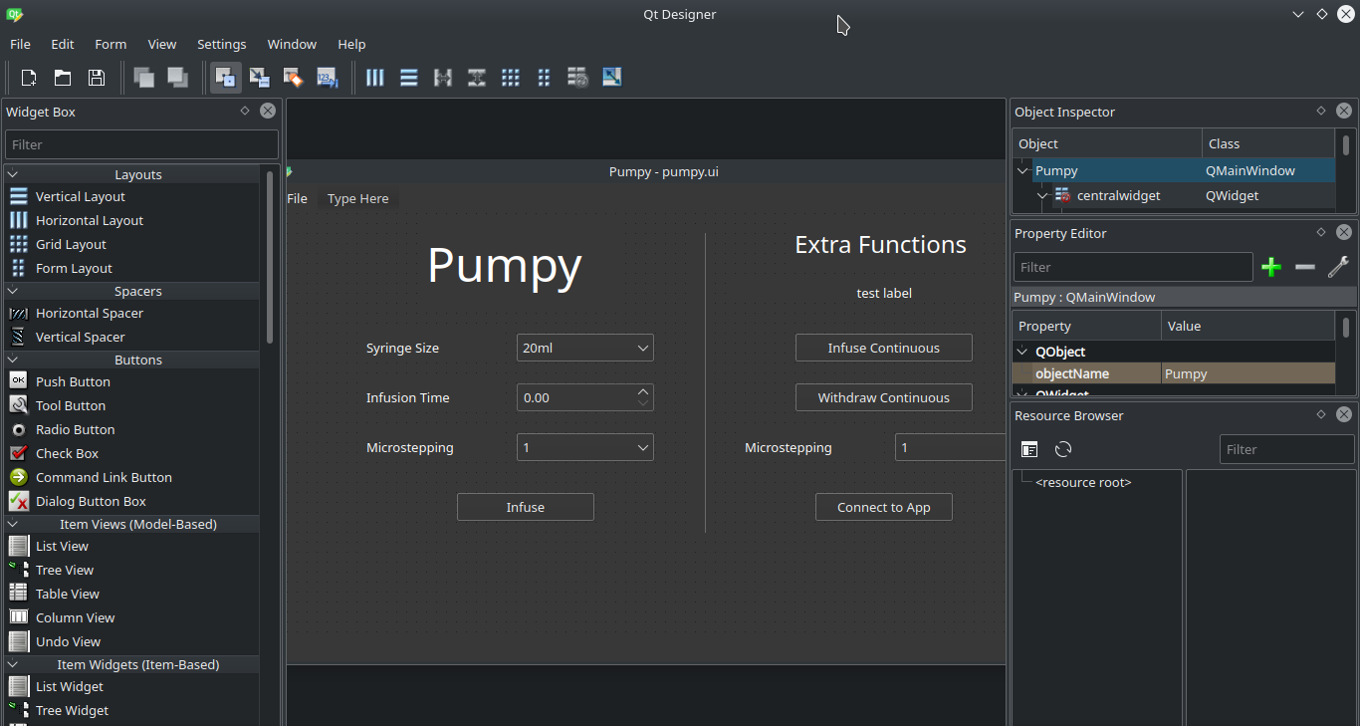
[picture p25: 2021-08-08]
documents/final-doc/images/qt-designer.png

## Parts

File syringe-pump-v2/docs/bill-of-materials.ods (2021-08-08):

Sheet: Sheet1
Hardware | Quantity | Cost per unit | Total Cost | Source | Cost for quantity | Notes
NEMA 17 Stepper Motor – 2A | 1 | £11.99 | £11.99 | eBay (UK) | £11.99 | Higher voltage = higher torque; torque curve tests at 24V, half step – going for 12V 2A initially
T8 200mm Threaded Rod | 1 | £5.49 | £5.49 | eBay (UK) | £5.49
8mm Steel Guide Rod | 2 | £3.34 | £6.68 | eBay (UK) | £6.68
688zz Bearing | 1 | £2.19 | £2.19 | eBay (UK) | £2.19
End Stop Limit Switch | 2 | £1.75 | £3.49 | eBay (UK) | £3.49
LM8SUU Linear Bearing | 2 | £1.90 | £3.80 | eBay (UK) | £3.80
T8 Lead Screw Nut (2mm Lead Round Flange) | 1 | £2.19 | £2.19 | eBay (UK) | £2.19
M3 Hex Nut | 16 | £2.89 | £2.89 | eBay (UK) | £2.89 | Pack of 25
M3 x 12mm Countersunk Screw | 4 | £1.75 | £1.75 | eBay (UK) | £1.75 | Pack of 10
M3 x 14mm Countersunk Screw | 4 | £2.49 | £2.49 | eBay (UK) | £2.49 | Pack of 10
M3 x 20mm Countersunk Screw | 4 | £2.79 | £2.79 | eBay (UK) | £2.79 | Pack of 10
M3 x 16mm Pan Head Screw | 4 | £1.99 | £1.99 | eBay (UK) | £1.99 | Pack of 10
M3 x 20mm Bolt | 2 | £1.49 | £1.49 | eBay (UK) | £1.49 | Pack of 10
M3 x 25mm Bolt | 2 | £1.49 | £1.49 | eBay (UK) | £1.49 | Pack of 10
M3 x 35mm Bolt | 4 | £1.90 | £1.90 | eBay (UK) | £1.90 | Pack of 10
Self-tapping Screw (2x8) | 2 | £1.98 | £1.98 | eBay (UK) | £1.98 | Pack of 10
Self-tapping Screw (2x10) | 4 | £2.70 | £2.70 | eBay (UK) | £2.70
Electronics
A4988 Stepper Driver | 1 | £2.50 | £2.50 | eBay (UK) | £2.50
12V DC Female Connector | 1 | £1.25 | £1.25 | eBay (UK) | £1.25
12V 2A Power Supply | 1 | £7.59 | £7.59 | eBay (UK) | £7.59 | Going with 12V/2A for initial testing, find cheap bench PSU/24V PSU
Cost without already owned components |  |  | £54.30 |  | £54.30
Raspberry Pi | 1 | £32.99 | £32.99 | eBay (UK) | £32.99 | Using a 3B since I own it
5 inch touchscreen – Waveshare | 1 | £44.59 | £44.59 | Amazon | £44.59 | New LCD touch display, doesn't use up GPIO ports
TOTAL |  |  |  |  | £146.22

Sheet: Sheet2
Hardware | Quantity | Cost per unit | Total Cost | Source | Cost for quantity
NEMA 17 Stepper Motor – 2A | 1 | £11.99 | £11.99 | eBay (UK) | £11.99
5mm Shaft Coupler | 1 | £4.25 | £4.25 | eBay (UK) | £4.25
625-Z Ball Bearing | 2 | £3.87 | £7.98 | eBay (UK) | £3.87
LM6UU Linear Bearing | 2 | £2.64 | £5.28 | eBay (UK) | £2.64
M3 x 10mm Cap Screws | 4 | £0.99 | £1.70 | eBay (UK) | £1.02
M3 x 20mm Cap Screws | 6 | £0.99 | £1.95 | eBay (UK) | £0.78
M3 x 40mm Cap Screws | 4 | £0.99 | £2.20 | eBay (UK) | £0.88
M3 Hex Nut | 12 | £0.99 | £2.89 | eBay (UK) | £1.50
M5 Hex Nut | 5 | £0.99 | £2.19 | eBay (UK) | £1.10
M5 Threaded Rod (200mm length) | 1 | £2.70 | £2.70 | eBay (UK) | £2.70
A2 Steel Rod (6mm diameter) (200mm length) | 2 | £2.99 | £5.98 | eBay (UK) | £5.98
Electronics
A4988 Stepper Driver | 1 | £2.50 | £2.50 | eBay (UK) | £2.50
12V DC Female Connector | 1 | £1.25 | £1.25 | eBay (UK) | £1.25
12V 2A Power Supply | 1 | £7.59 | £7.59 | eBay (UK) | £7.59
Cost without already owned components |  |  | £60.45 |  | £48.05
Raspberry Pi | 1 | £32.99 | £32.99 | eBay (UK) | £32.99
5 inch touchscreen – Elecrow | 1 | £30.99 | £30.99 | Amazon | £30.99

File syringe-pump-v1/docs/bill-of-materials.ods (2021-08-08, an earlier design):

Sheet: Sheet1
Arrived | Hardware | Quantity | Cost per unit | Total Cost | Source | Cost for quantity | Notes
y | NEMA 17 Stepper Motor – 2A | 1 | £11.99 | £11.99 | eBay (UK) | £11.99 | Higher voltage = higher torque; torque curve tests at 24V, half step – going for 12V 2A initially
y | 5mm Shaft Coupler | 1 | £4.25 | £4.25 | eBay (UK) | £4.25
 | 625-Z Ball Bearing | 2 | £3.87 | £7.98 | eBay (UK) | £3.87 | FAG/SKF – brand names
y | LM6UU Linear Bearing | 2 | £2.64 | £5.28 | eBay (UK) | £2.64 | comes with rubber seals, should be fine
y | M3 x 10mm Cap Screws | 6 | £0.99 | £1.70 | eBay (UK) | £1.02 | Pack of 10 = Total cost
y | M3 x 20mm Cap Screws | 4 | £0.99 | £1.95 | eBay (UK) | £0.78 | Pack of 10 = Total cost
y | M3 x 40mm Cap Screws | 4 | £0.99 | £2.20 | eBay (UK) | £0.88 | Pack of 10 = Total cost
y | M3 Hex Nut | 13 | £0.99 | £2.89 | eBay (UK) | £1.50 | Pack of 25 = Total cost
y | M5 Hex Nut | 5 | £0.99 | £2.19 | eBay (UK) | £1.10 | Pack of 10 = Total cost
y | M5 Threaded Rod (200mm length) | 1 | £2.70 | £2.70 | eBay (UK) | £2.70 | Ordered 3, total = 5.15
y | A2 Steel Rod (6mm diameter) (200mm length) | 2 | £2.99 | £5.98 | eBay (UK) | £5.98
 | Electronics
y | A4988 Stepper Driver | 1 | £2.50 | £2.50 | eBay (UK) | £2.50
y | 12V DC Female Connector | 1 | £1.25 | £1.25 | eBay (UK) | £1.25
y | 12V 2A Power Supply | 1 | £7.59 | £7.59 | eBay (UK) | £7.59 | Going with 12V/2A for initial testing, find cheap bench PSU/24V PSU
 | Cost without already owned components |  |  | £60.45 |  | £48.05
y | Raspberry Pi | 1 | £32.99 | £32.99 | eBay (UK) | £32.99 | Using a 3B since I own it
y | 5 inch touchscreen – Elecrow | 1 | £30.99 | £30.99 | Amazon | £30.99 | not required for this version (sp-v1)
 | TOTAL |  |  |  |  | £81.04

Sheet: Sheet2
Hardware | Quantity | Cost per unit | Total Cost | Source | Cost for quantity
NEMA 17 Stepper Motor – 2A | 1 | £11.99 | £11.99 | eBay (UK) | £11.99
5mm Shaft Coupler | 1 | £4.25 | £4.25 | eBay (UK) | £4.25
625-Z Ball Bearing | 2 | £3.87 | £7.98 | eBay (UK) | £3.87
LM6UU Linear Bearing | 2 | £2.64 | £5.28 | eBay (UK) | £2.64
M3 x 10mm Cap Screws | 4 | £0.99 | £1.70 | eBay (UK) | £1.02
M3 x 20mm Cap Screws | 6 | £0.99 | £1.95 | eBay (UK) | £0.78
M3 x 40mm Cap Screws | 4 | £0.99 | £2.20 | eBay (UK) | £0.88
M3 Hex Nut | 12 | £0.99 | £2.89 | eBay (UK) | £1.50
M5 Hex Nut | 5 | £0.99 | £2.19 | eBay (UK) | £1.10
M5 Threaded Rod (200mm length) | 1 | £2.70 | £2.70 | eBay (UK) | £2.70
A2 Steel Rod (6mm diameter) (200mm length) | 2 | £2.99 | £5.98 | eBay (UK) | £5.98
Electronics
A4988 Stepper Driver | 1 | £2.50 | £2.50 | eBay (UK) | £2.50
12V DC Female Connector | 1 | £1.25 | £1.25 | eBay (UK) | £1.25
12V 2A Power Supply | 1 | £7.59 | £7.59 | eBay (UK) | £7.59
Cost without already owned components |  |  | £60.45 |  | £48.05
Raspberry Pi | 1 | £32.99 | £32.99 | eBay (UK) | £32.99
5 inch touchscreen – Elecrow | 1 | £30.99 | £30.99 | Amazon | £30.99

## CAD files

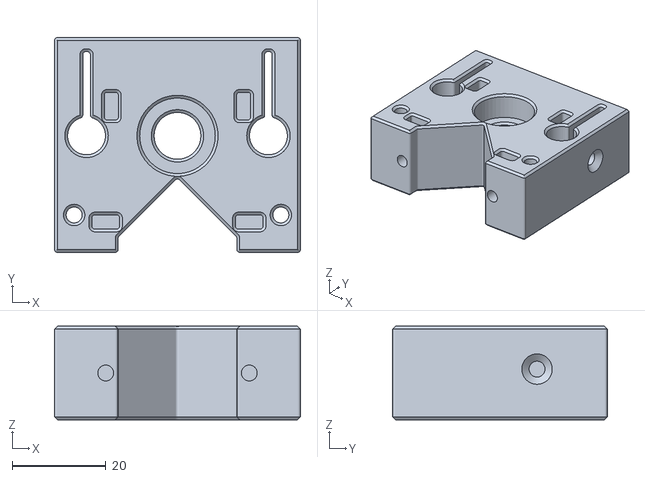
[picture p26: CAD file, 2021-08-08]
syringe-pump-v2/stl-files/frontSupport.stl
52.6 x 45.9 x 20.0

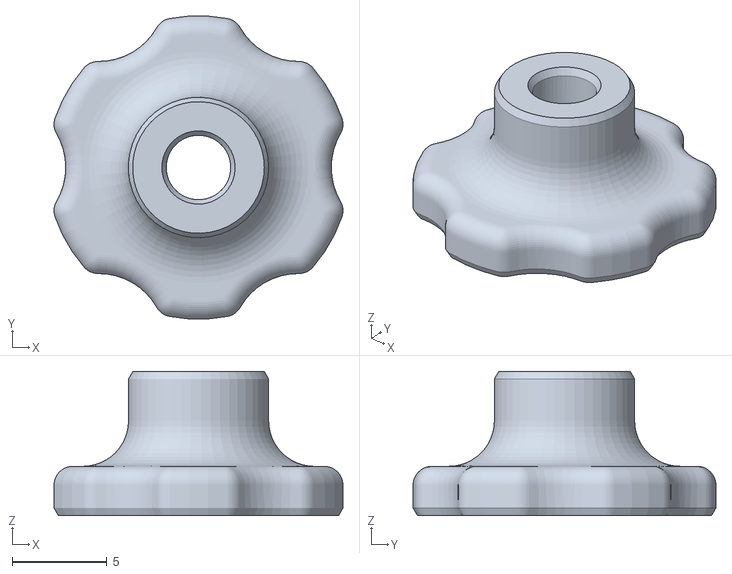
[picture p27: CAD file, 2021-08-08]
syringe-pump-v2/stl-files/handKnob7mm.stl
15.2 x 16.0 x 7.60

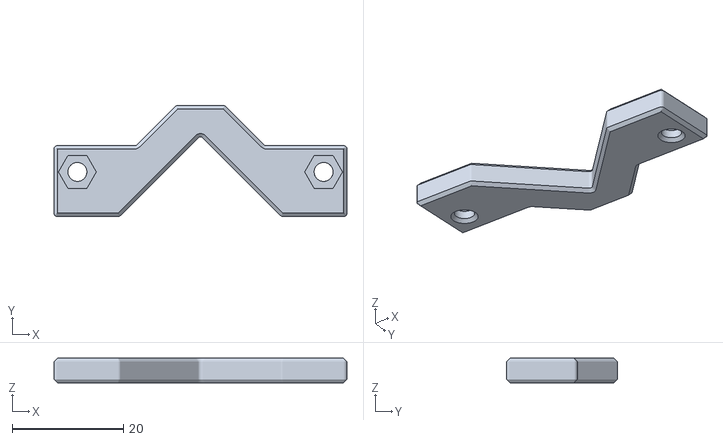
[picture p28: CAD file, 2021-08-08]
syringe-pump-v2/stl-files/sideSyringeHolder.stl
52.6 x 19.9 x 4.40

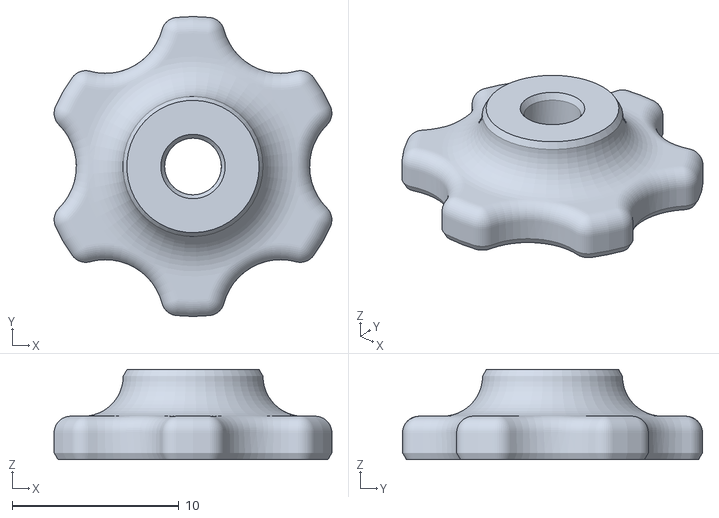
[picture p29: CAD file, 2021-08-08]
syringe-pump-v2/stl-files/handKnob9mm.stl
16.7 x 18.0 x 5.40

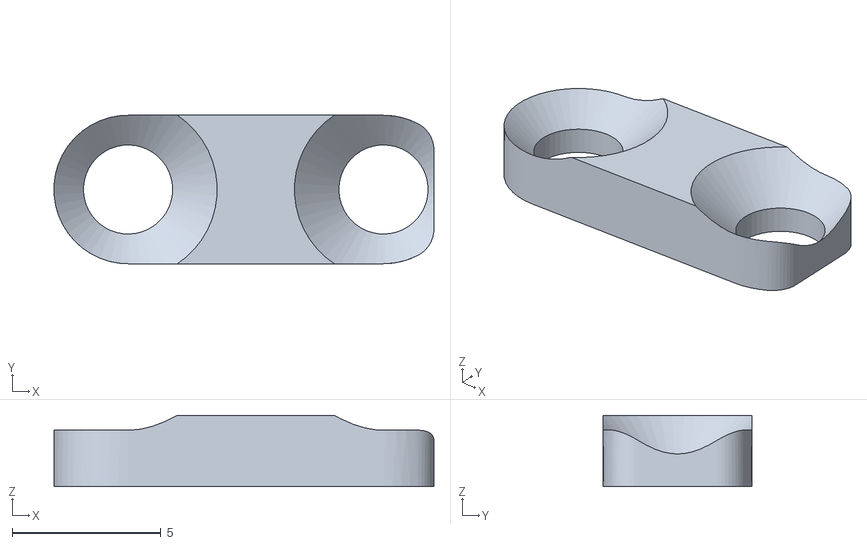
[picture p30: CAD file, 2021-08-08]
syringe-pump-v2/stl-files/wireHolder.stl
12.8 x 5.00 x 2.40

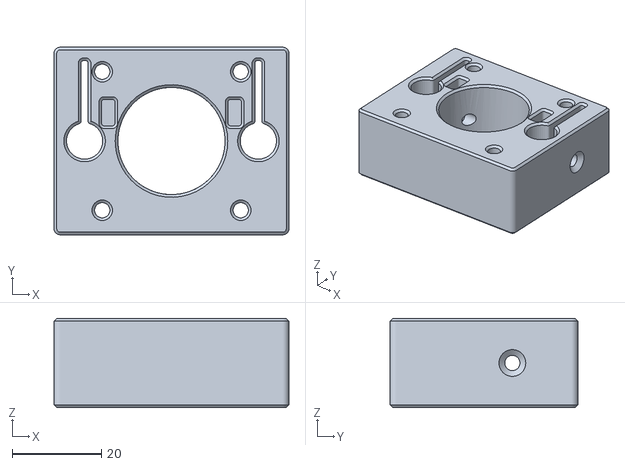
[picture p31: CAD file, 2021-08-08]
syringe-pump-v2/stl-files/backSupport.stl
52.6 x 42.0 x 20.0

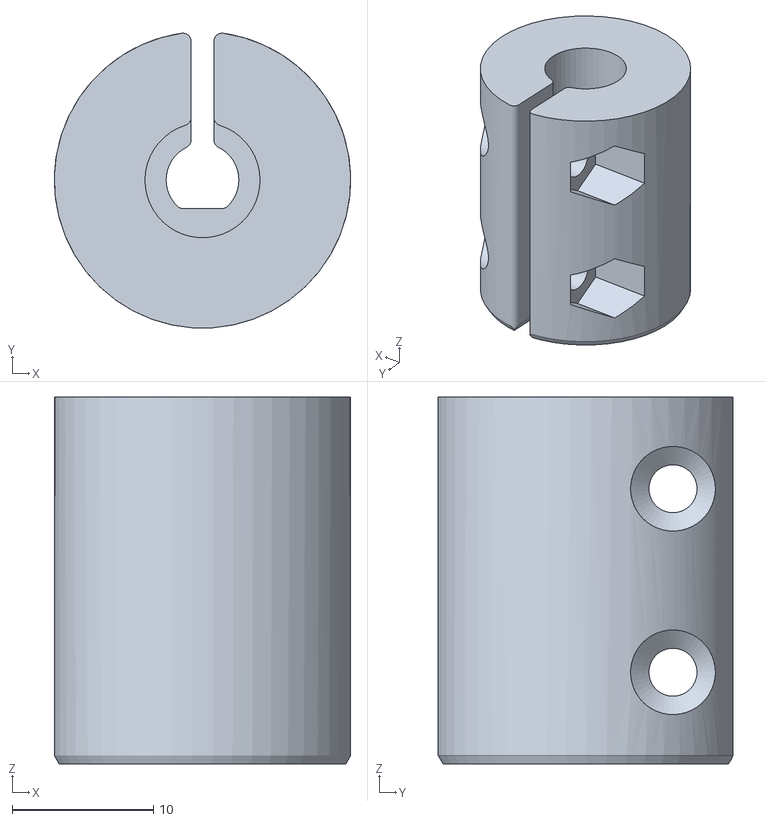
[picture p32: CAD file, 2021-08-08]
syringe-pump-v2/stl-files/coupling.stl
21.0 x 20.9 x 26.0

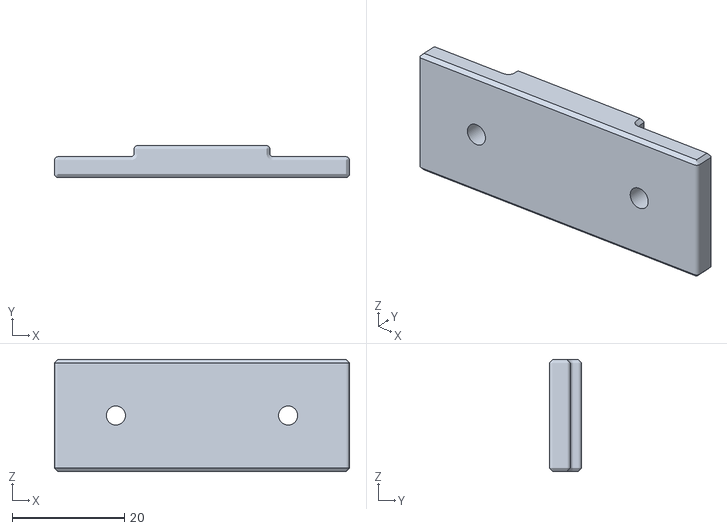
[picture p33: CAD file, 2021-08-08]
syringe-pump-v2/stl-files/topSyringeHolder25mm.stl
52.6 x 5.70 x 20.0

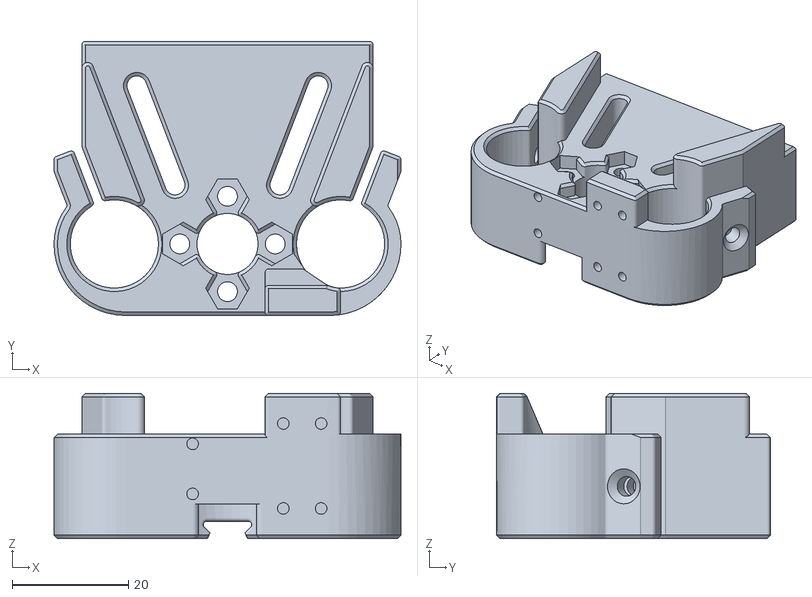
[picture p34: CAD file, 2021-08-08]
syringe-pump-v2/stl-files/carriage.stl
59.7 x 47.1 x 25.0

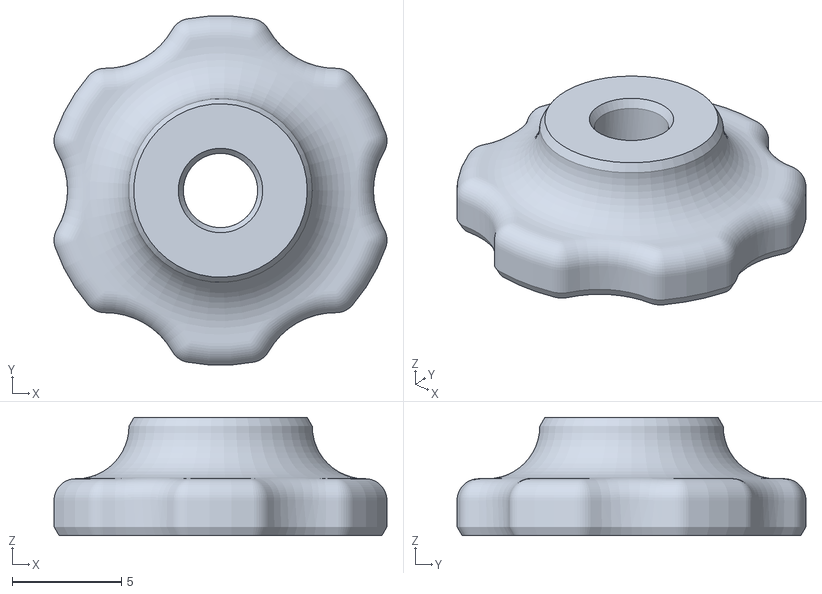
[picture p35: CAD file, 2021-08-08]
syringe-pump-v2/stl-files/handKnob8mm.stl
15.2 x 16.0 x 5.40

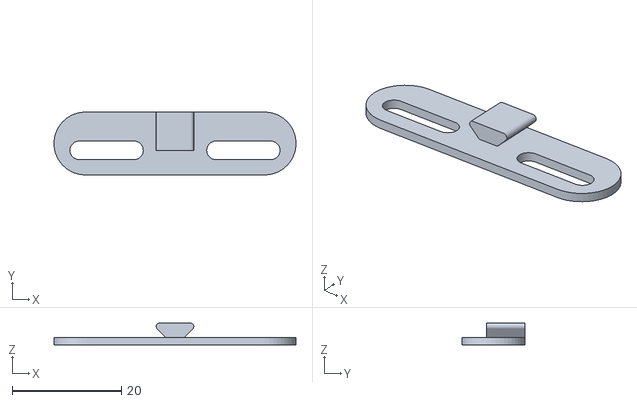
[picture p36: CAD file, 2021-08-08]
syringe-pump-v2/stl-files/slider.stl
44.2 x 11.5 x 4.00

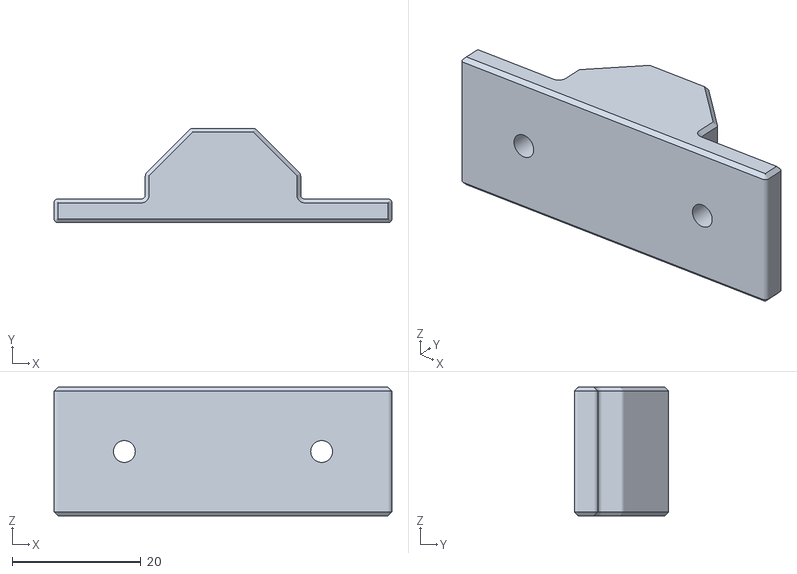
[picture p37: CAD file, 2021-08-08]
syringe-pump-v2/stl-files/topSyringeHolder12mm.stl
52.6 x 14.7 x 20.0

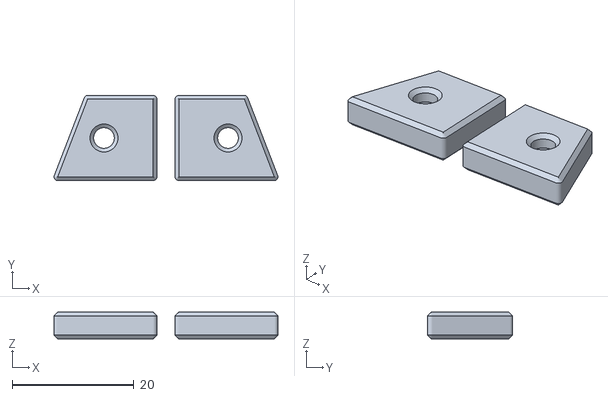
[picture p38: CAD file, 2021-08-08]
syringe-pump-v2/stl-files/plungerHolders.stl
36.8 x 14.0 x 4.40

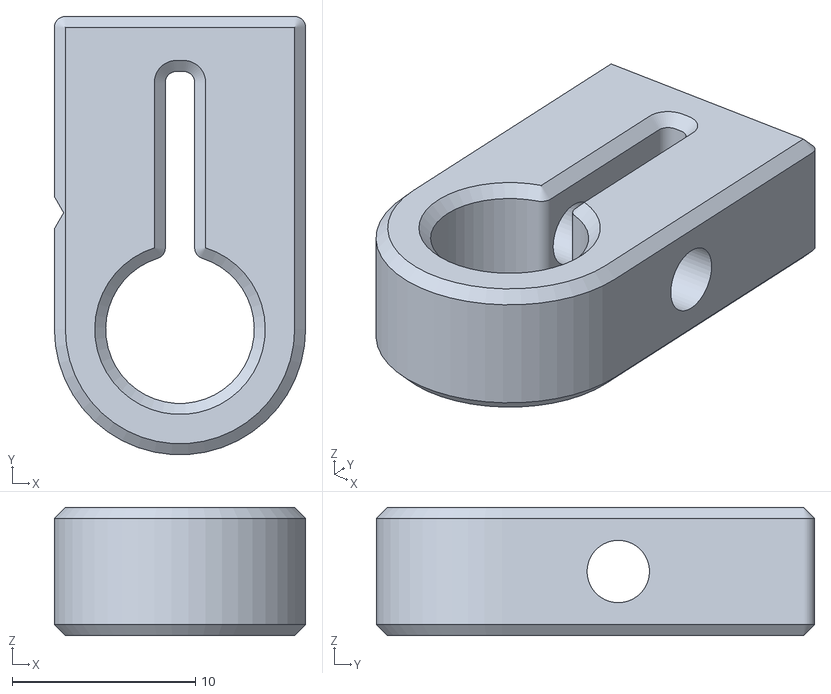
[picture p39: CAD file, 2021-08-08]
syringe-pump-v2/stl-files/limitStop.stl
13.7 x 23.9 x 7.00

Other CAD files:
syringe-pump-v1/stl-files/motor-end.stl
syringe-pump-v1/stl-files/unused-files/linear_actuator_v0-8.stl
syringe-pump-v1/stl-files/idler-end.stl
syringe-pump-v1/stl-files/unused-files/linear_actuator_v0-6.stl
syringe-pump-v1/stl-files/carriage-modified.stl
syringe-pump-v1/stl-files/carriage-unmodified.stl
syringe-pump-v1/stl-files/plunger-holder-base-and-tab.stl
syringe-pump-v1/stl-files/syringe-body-holder-unmodified.stl
syringe-pump-v1/stl-files/syringe-holder-modified.stl
syringe-pump-v1/stl-files/unused-files/carriage-notop-unmodified.stl

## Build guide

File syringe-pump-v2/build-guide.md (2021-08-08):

# Syringe Pump v2

Syringe Pump v2 Image

---
## Parts List

### Tools

* 2mm Allen Key
* 3mm Allen Key
* Phillips Head Screwdriver
* Soldering Iron
* Solder
* Wires
* Super Glue (optional)

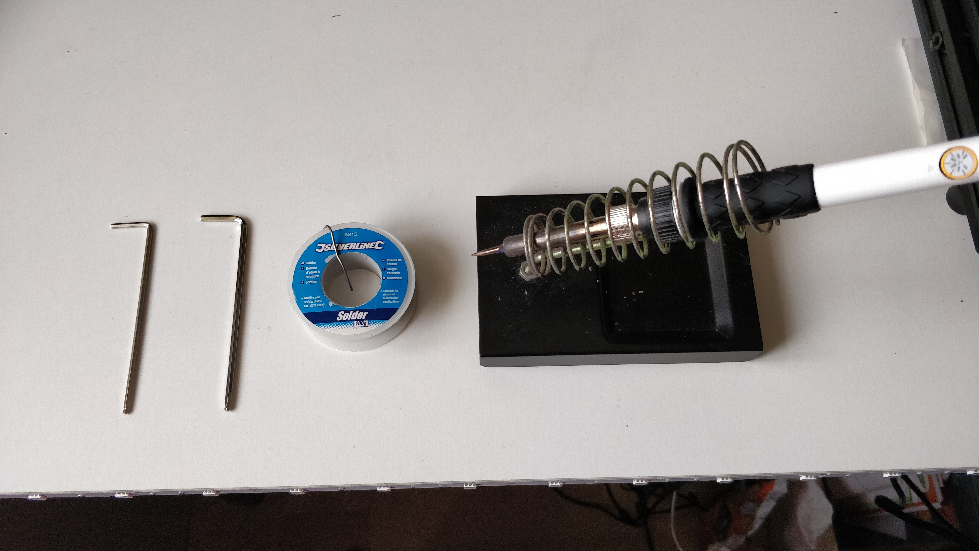
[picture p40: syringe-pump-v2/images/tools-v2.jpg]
Image of tools


### 3D Printed Parts

* [Back Support](./stl-files/backSupport.stl)
* [Coupling](./stl-files/coupling.stl)
* [Carriage](./stl-files/carriage.stl)
* [Limit Stop (x2)](./stl-files/limitStop.stl)
* [Front Support](./stl-files/frontSupport.stl)
* [Wire Holder](./stl-files/wireHolder.stl)
* [Plunger Holders](./stl-files/plungerHolders.stl)
* [Side Syringe Holder](./stl-files/sideSyringeHolder.stl)
* [Slider](./stl-files/slider.stl)
* [7mm Hand Knobs (x2)](./stl-files/handKnob7mm.stl)
* [8mm Hand Knobs (x2)](./stl-files/handKnob8mm.stl)
* [9mm Hand Knobs (x2)](./stl-files/handKnob9mm.stl)

### Bill of Materials Spreadsheet

Bill of Materials Spreadsheet

### Exploded Parts View

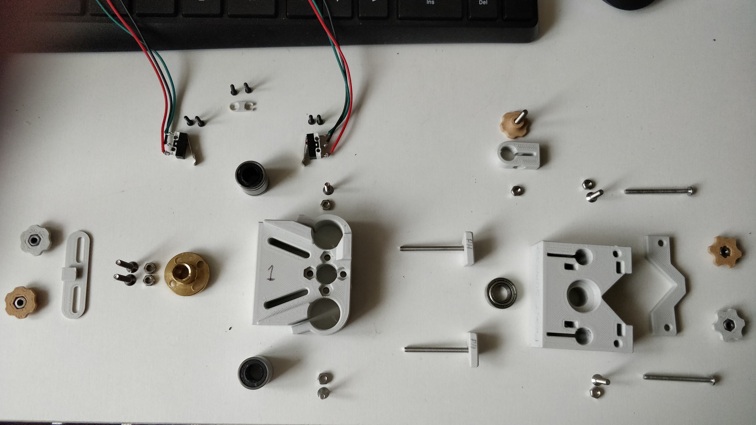
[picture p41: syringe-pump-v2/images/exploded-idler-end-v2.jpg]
Exploded Front End

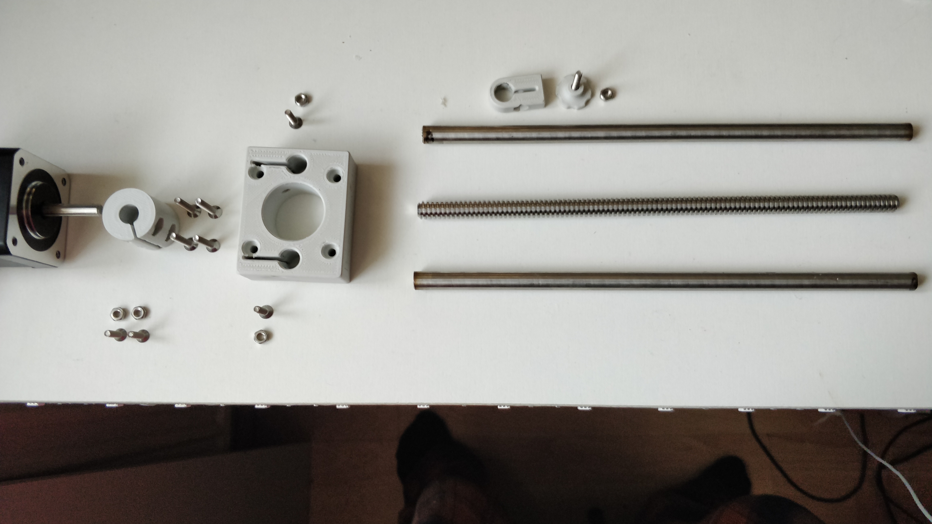
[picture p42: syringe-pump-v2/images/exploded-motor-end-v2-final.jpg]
Exploded Motor End


---
## Build Guide

1. Using 2 M3 x 12mm Countersunk Screws and 2 M3 Hex Nuts, attach the coupling to the motor and the
   threaded rod

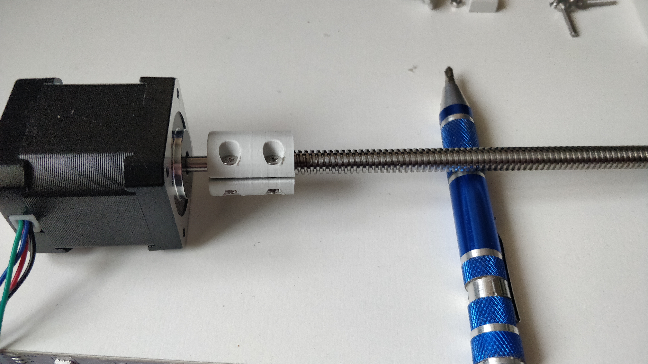
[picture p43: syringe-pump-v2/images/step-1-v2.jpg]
Step 1 Image


2. Using 4 M3 x 20mm Countersunk Screws and 2 M3 Hex Nuts, insert the nuts into the Back Support, slide it through the
   threaded rod and screw it into the motor

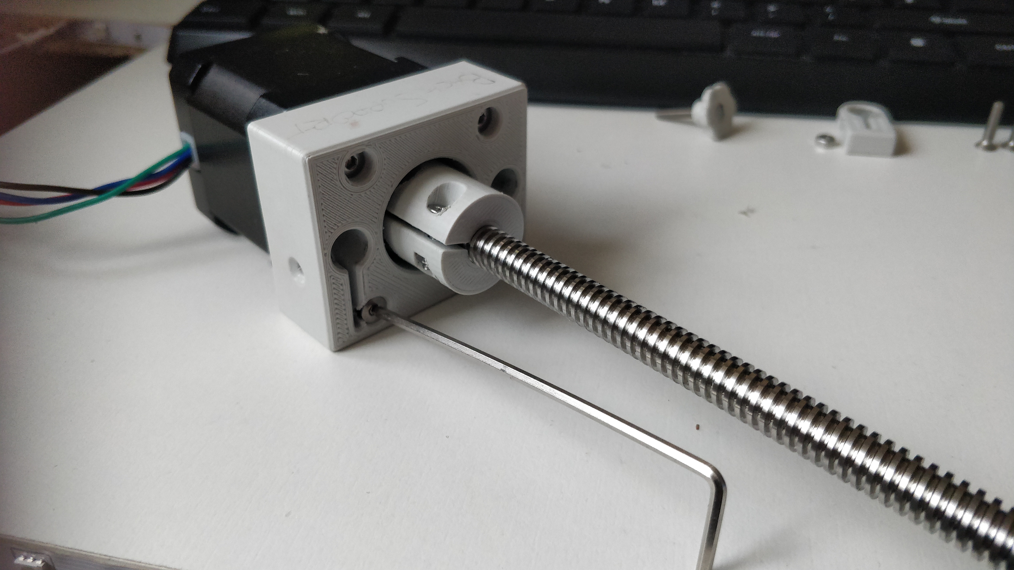
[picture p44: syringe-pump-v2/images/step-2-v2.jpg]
Step 2 Image


3. Using 2 M3 x 14mm Countersunk Screws, insert the 2 steel rods into the holes and tighten them in with
   the screws

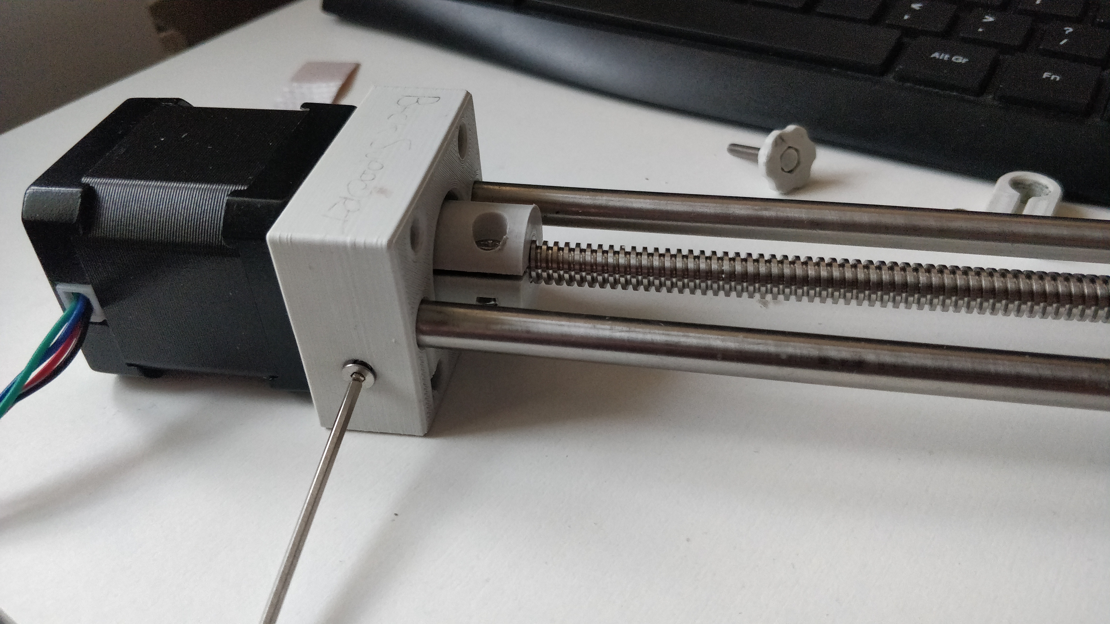
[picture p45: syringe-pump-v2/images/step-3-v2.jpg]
Step 3 Image


4. Assemble the 2 Limit Stops using 2 7mm Hand Knobs, 2 M3 Nuts and 2 M3 x 20mm Bolts - to make this easier
   you can super glue the bolt head into the Hand Knob.

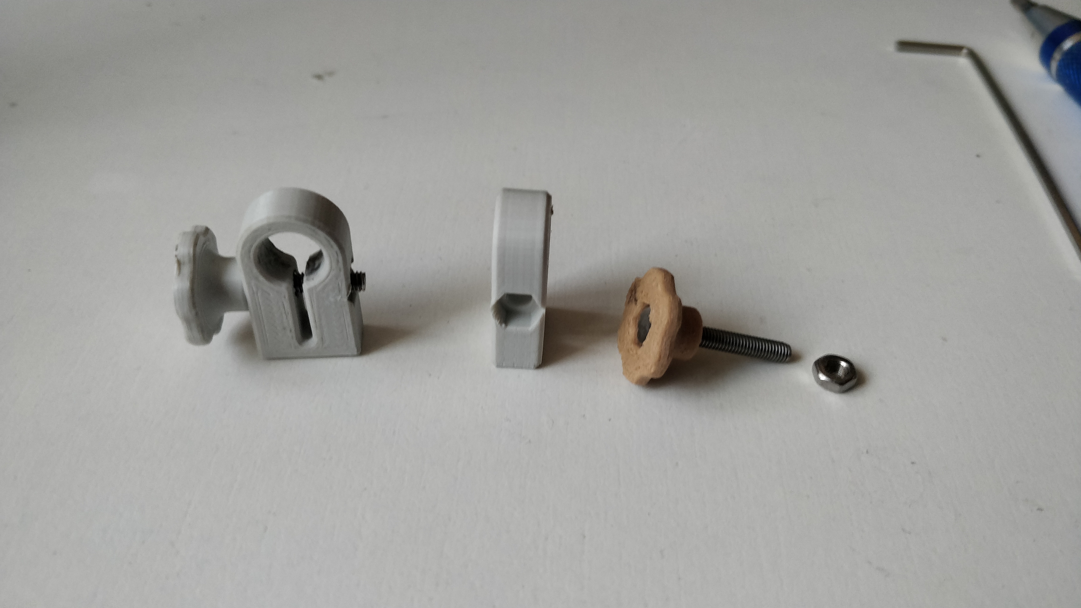
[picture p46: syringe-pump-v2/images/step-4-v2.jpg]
Step 4 Image


5. Take the Carriage and insert the 2 linear bearings, then use 2 M3 Hex Nuts and 2 M3 x 12mm Countersunk Screws
   on the side of the Carriage to hold the bearings inside

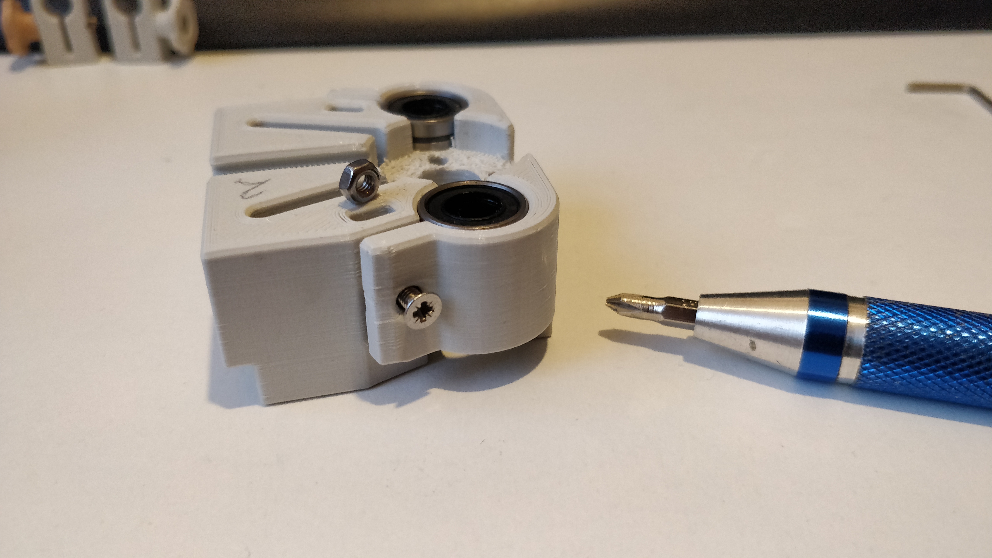
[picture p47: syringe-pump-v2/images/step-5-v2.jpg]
Step 5 Image


6. Using 2 M3 x 16mm Pan Head Screws and 2 M3 Hex Nuts, attach the T8 Lead Screw Nut into the Carriage and tighten
   the top and bottom holes

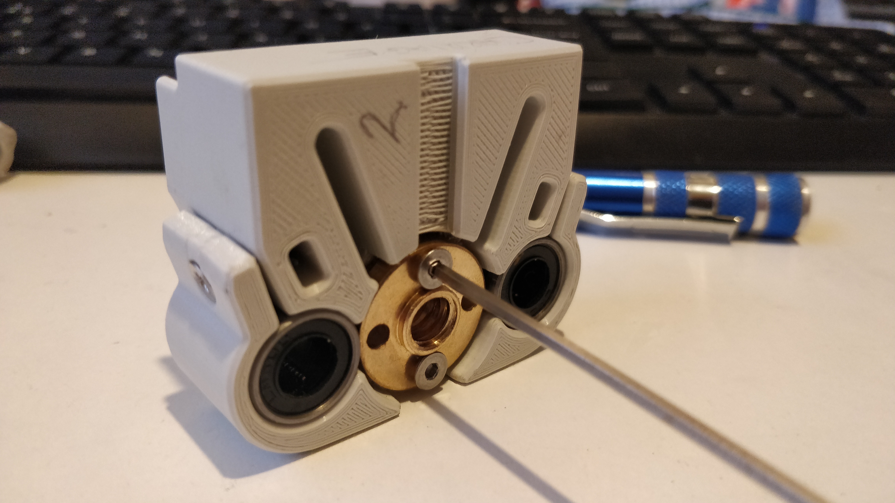
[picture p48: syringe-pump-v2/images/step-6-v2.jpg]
Step 6 Image


7. De-solder the Limit Switches from their breakout boards, cut 6 equal lengths of wire and solder them to the 6
   terminals of the limit switches

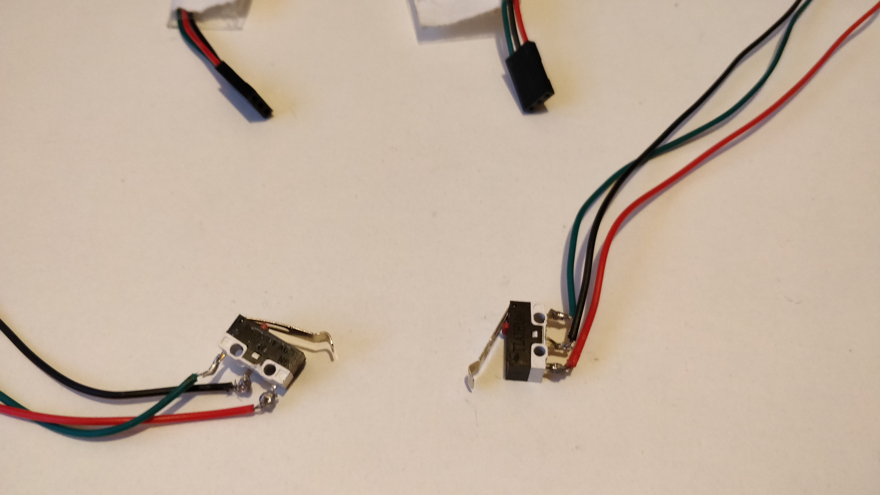
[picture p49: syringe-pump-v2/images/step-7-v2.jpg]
Step 7 Image


8. Using 4 2x10 Self-tapping screws, attach the Limit Switches to the underside of the carriage, then feed the wires
   along the base and secure them with the Wire Holder and 2 2x8 Self-tapping screws

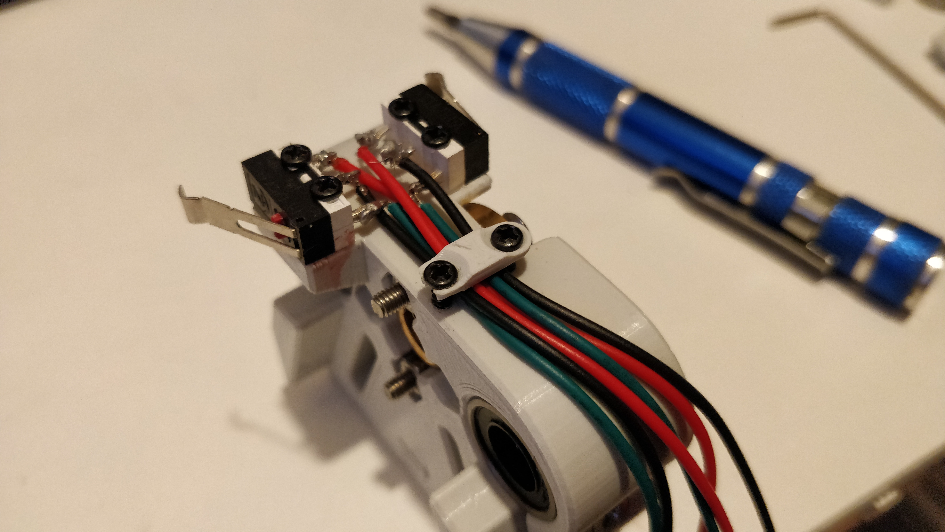
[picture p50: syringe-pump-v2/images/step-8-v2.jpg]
Step 8 Image


9. Slide 2 M3 x 35mm Bolts into the Plunger Holders, insert 2 M3 Hex Nuts into the 2 8mm Hand Knobs, push the Slider
   into the Carriage and insert the Plunger Holders into the gaps on the slider from the other side, tightening them with the Hand Knobs onto the Slider side

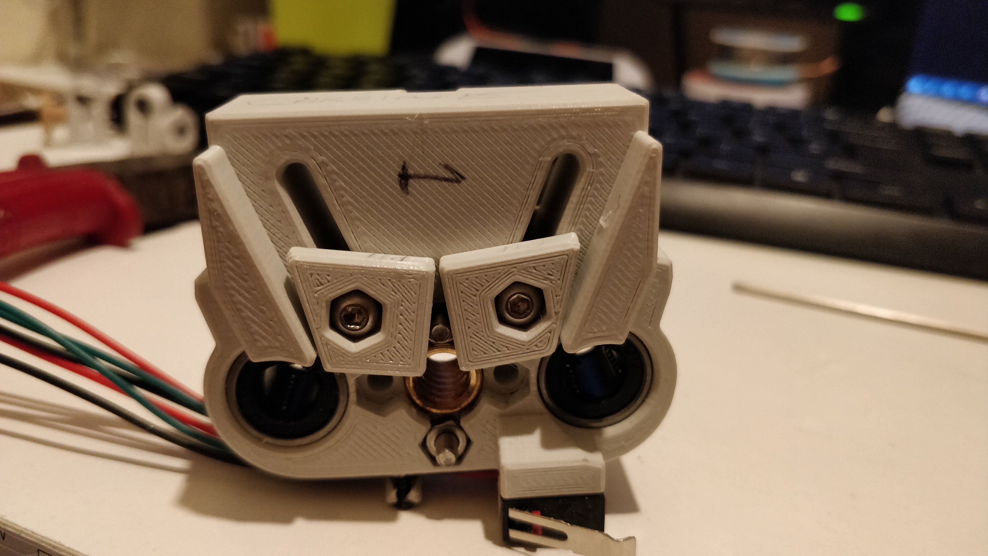
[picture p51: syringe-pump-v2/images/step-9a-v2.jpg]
Step 9a Image

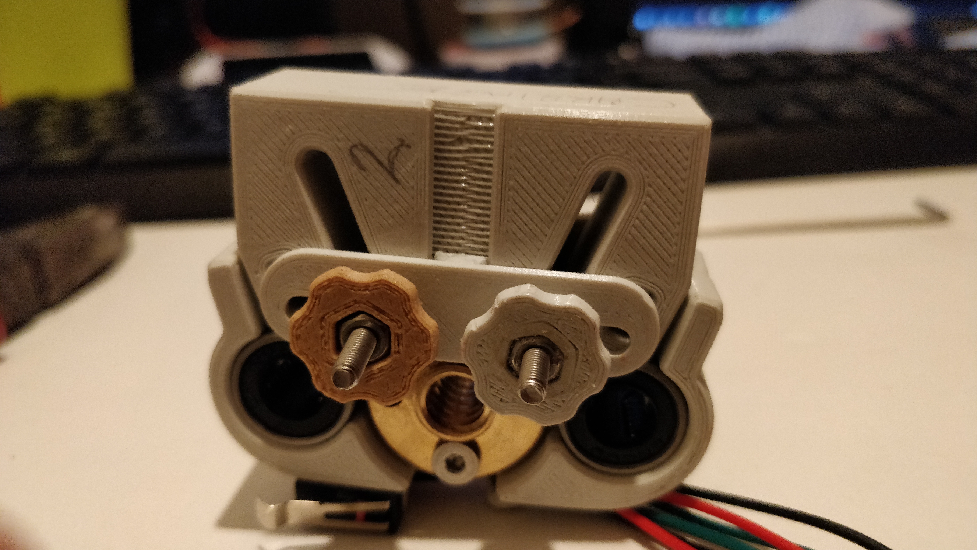
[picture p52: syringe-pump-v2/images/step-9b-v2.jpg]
Step 9b Image


10. Slide the first Limit Stop onto the left steel rod, then push the Carriage onto the threaded rod (Plunger Holders
    facing away from the motor) and twist the coupling counter-clockwise to bring the carriage along the rod. Then slide
    the other Limit Stop onto the left steel rod

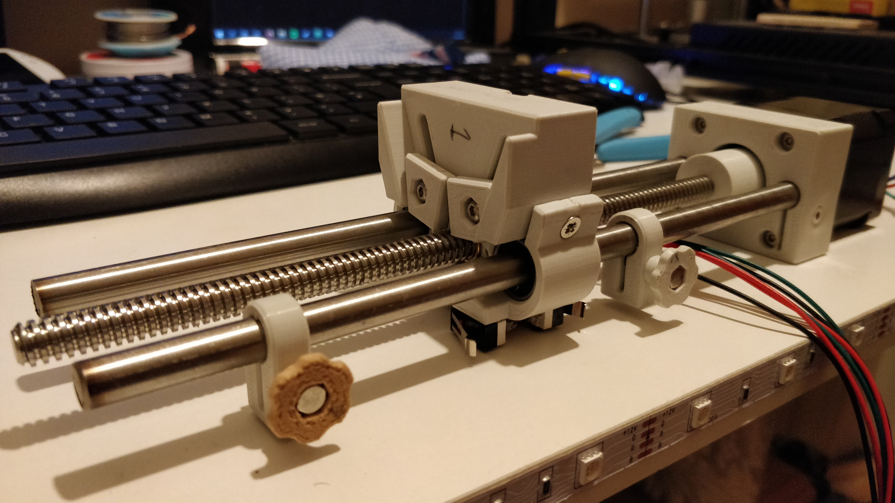
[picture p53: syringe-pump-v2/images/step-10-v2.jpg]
Step 10 Image


11. Push the 688ZZ bearing into the Front Support, using 2 M3 x 35mm Bolts attach the Side Syringe Holder to the side of
    the Front Support where the bearing is and use 2 9mm Hand Knobs and 2 M3 Hex Nuts on the other side of the bolts to
    adjust the tightness of the Side Syringe Holder

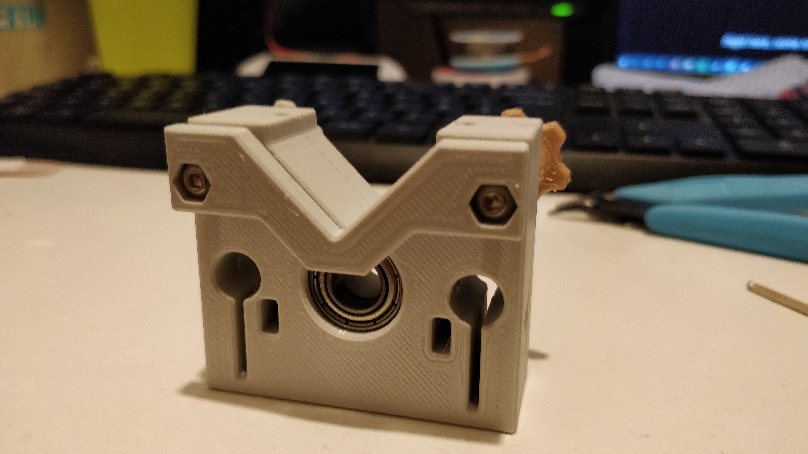
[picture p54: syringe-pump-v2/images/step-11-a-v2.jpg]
Step 11 Image

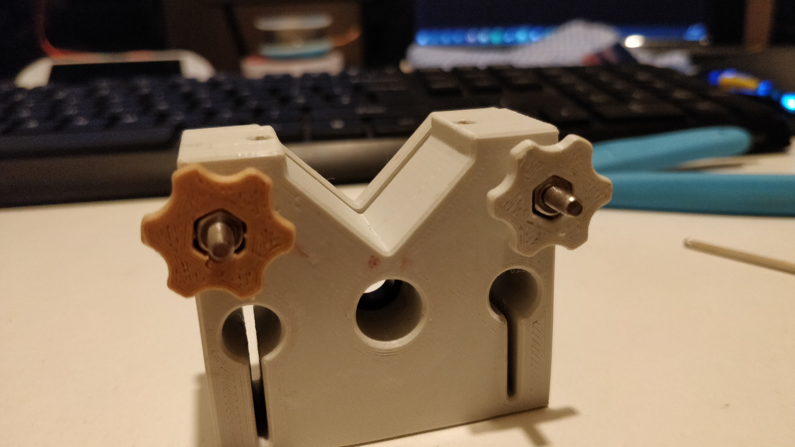
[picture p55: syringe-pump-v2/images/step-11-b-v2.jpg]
Step 11 Image


12. Slide 2 M3 Hex Nuts into the Front Support, slide it onto the end of the rods and tighten it using 2 M3 x 14mm
    Countersunk Screws

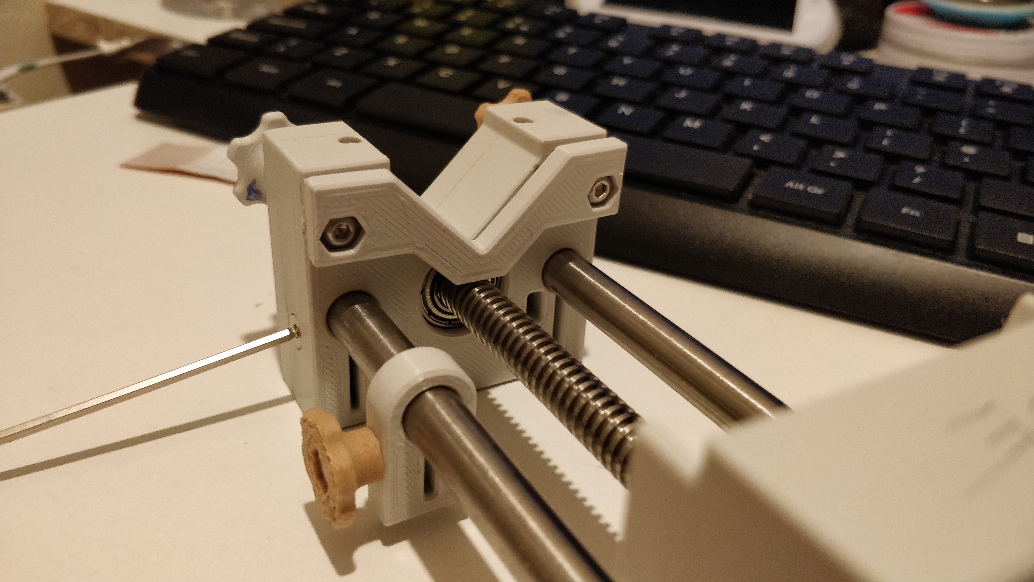
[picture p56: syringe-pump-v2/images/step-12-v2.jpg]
Step 12 Image


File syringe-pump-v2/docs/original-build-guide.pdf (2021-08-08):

# Open-Source Syringe Pump

(developed by Andrey Samokhin in 2018)

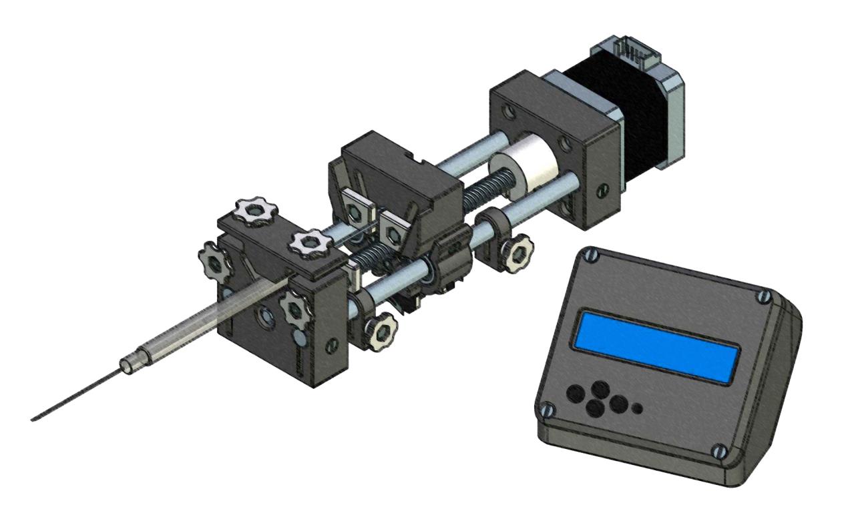
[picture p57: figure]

# Assembly Instructions

(Version 1.0a)

STL-files and "firmware" are available at http://www.mass-spec.ru/projects/diy/syringe_pump/eng/
Project files are distributed under CC BY-SA 3.0 license

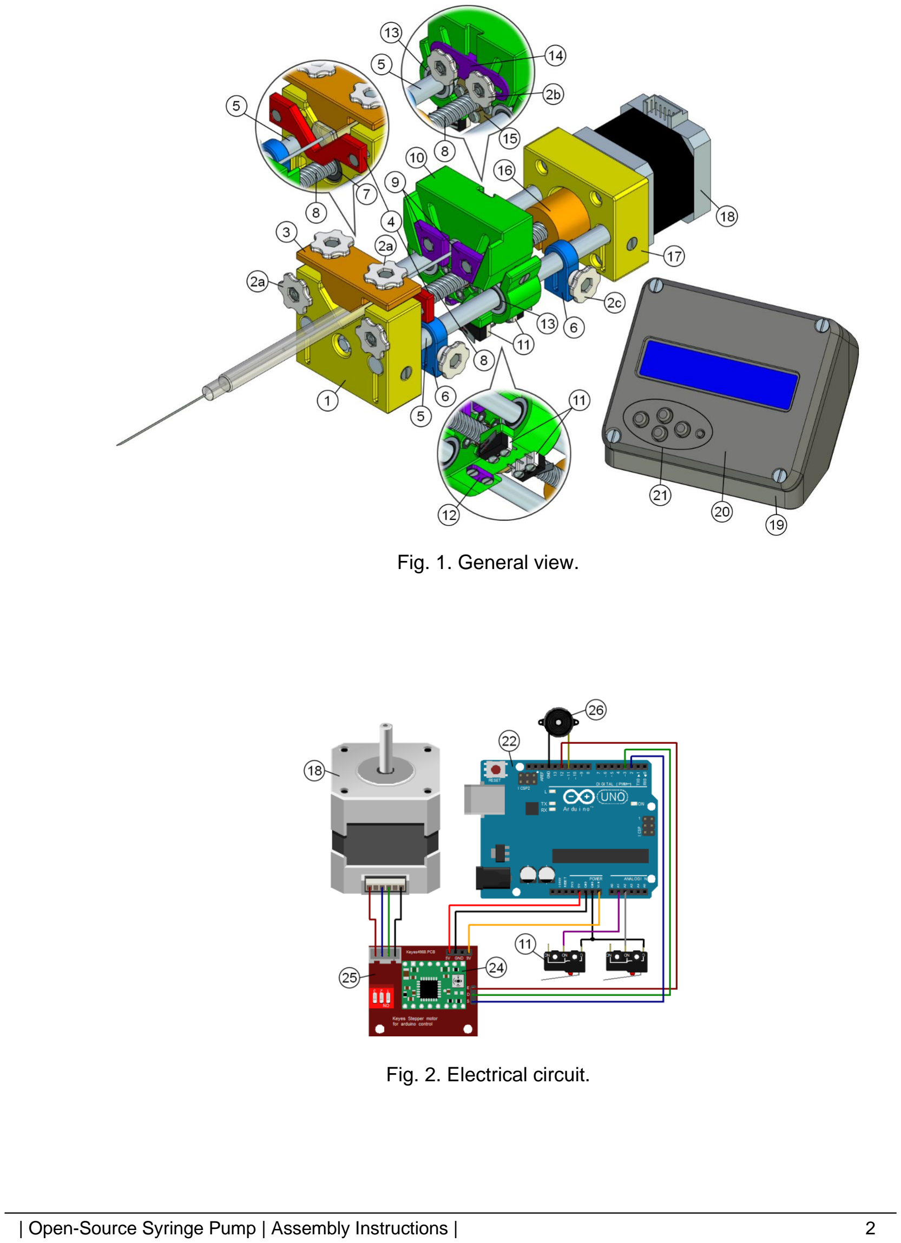
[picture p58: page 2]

| Open-Source Syringe Pump | Assembly Instructions | | 2

Fig. 1. General view.

Fig. 2. Electrical circuit.

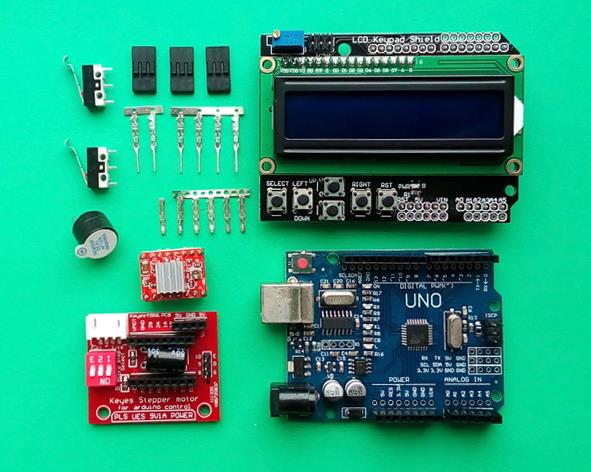
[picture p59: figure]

Fig. 3. Electronic components.

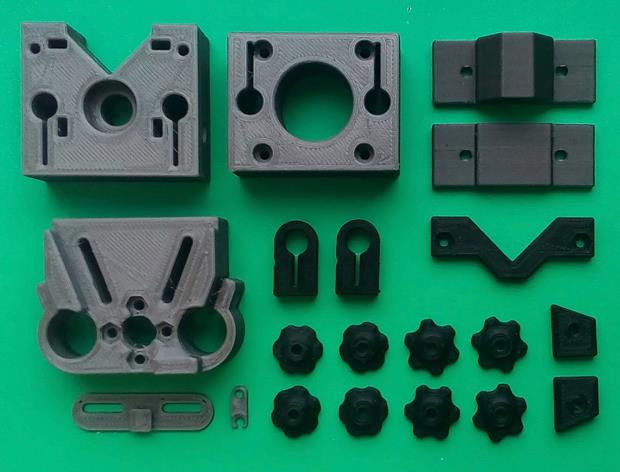
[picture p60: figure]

Fig. 4. Plastic parts made on 3D printer.

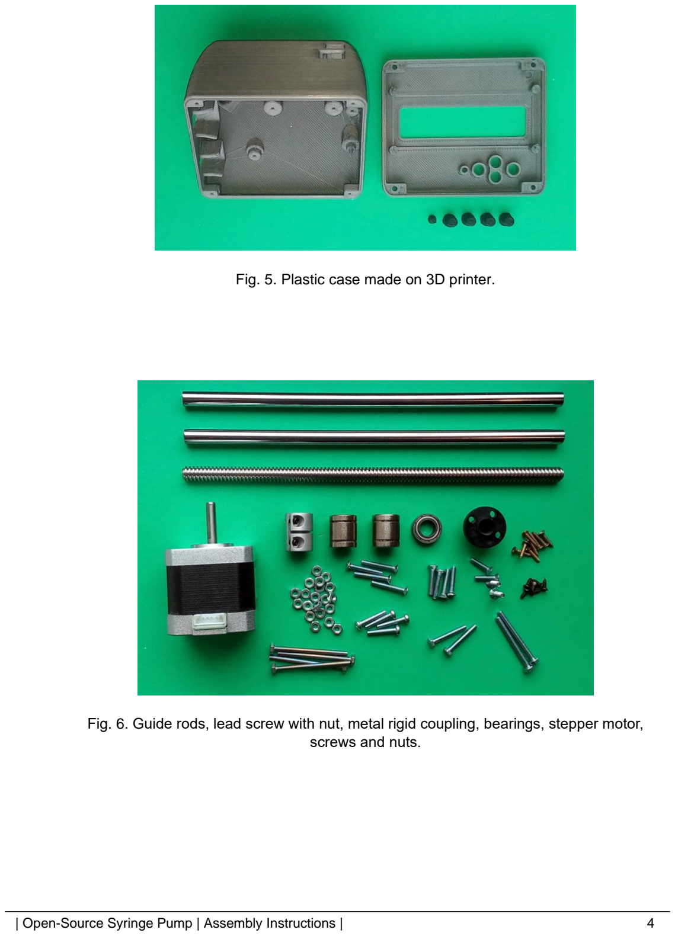
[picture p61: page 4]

Fig. 5. Plastic case made on 3D printer.

Fig. 6. Guide rods, lead screw with nut, metal rigid coupling, bearings, stepper motor, screws and nuts.

| Open

-Source Syringe Pump | Assembly Instructions |
5

Table 1. Part list.

PART # | PART NAME Front Support | QTY 1 1
2a | Hand Knob (9 mm) | 4
2b | Hand Knob (8 mm) | 2
2c | Hand Knob (7 mm) | 2
3 | Top Syringe Holder | 1
4 | Side Syringe Holder | 1
5 | Guide Rod (D=8 mm) | 2
6 | Limit Stop | 2
7 | Bearing 688ZZ | 1
8 | Lead Screw (T8) | 1
9 | Plunger Holders | 1
10 | Carriage | 1
11 | Endstop Switch | 2
12 | Wire Holder | 1
13 | Linear Bearing (LM8SUU) | 2
14 | Slider | 1
15 | Lead Screw Nut (T8) | 1
16 | Coupling | 1
17 | Back Support | 1
18 | Stepper Motor (NEMA 17) | 1
19 | Case (Base ) | 1
20 | Case (Cover ) | 1
21 | Buttons | 1
22 | Arduino UNO | 1
23 | LCD Keypad Shield | 1
24 | Stepper Motor Driver (A4988) | 1
25 | Control Shield for A4988 | 1
26 | Active Buzzer (D=12 mm) | 1
27 | Nut M3 | 20
28 | Countersunk Screw M3x12 | 4
29 | Countersunk Screw M3x14 | 4
30 | Countersunk Screw M3x20 | 4
31 | Pan Head Screw M3x16 | 4
32 | Bolt M3x20 | 2
33 | Bolt M3x25 | 2
34 | Bolt M3x35 | 4
35 | Self -tapping Screw 2x8 | 6
36 | Self -tapping Screw 2x10 | 8
37 | Dupont Connector (Female) | 6
38 | Dupont Connector (Male) | 6
39 | Dupont Housing (3P) | 3
40 | Connector Wires | –
41 | Power Supply (12 V, 2 A) | 1

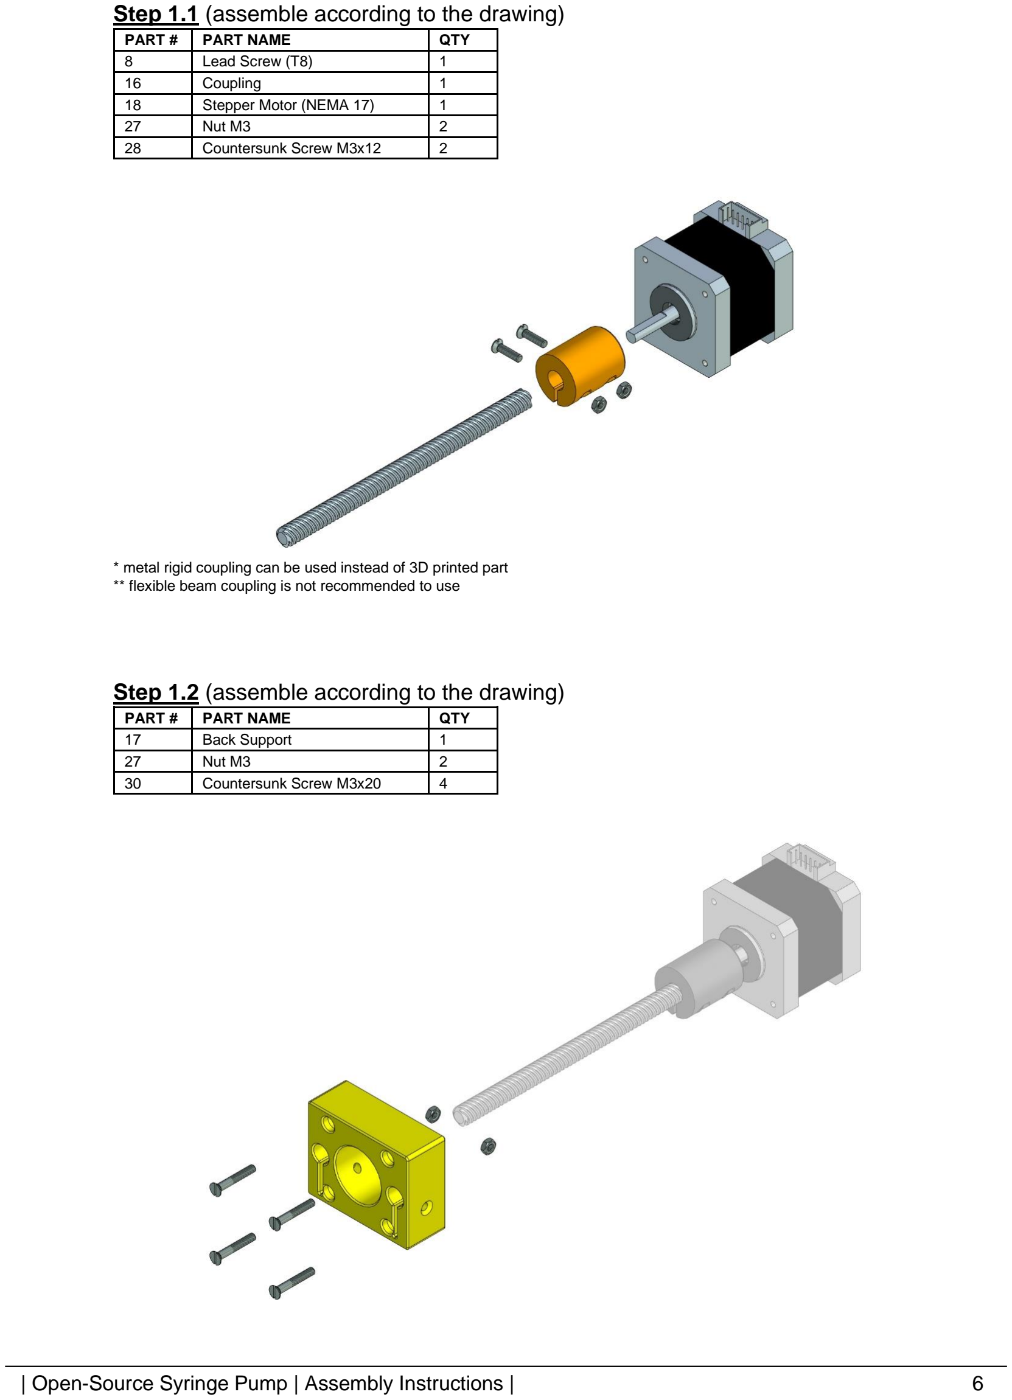
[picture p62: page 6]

Step 1.1 (assemble according to the drawing)
PART # | PART NAME | QTY
8 | Lead Screw (T8) | 1
16 | Coupling | 1
18 | Stepper Motor (NEMA 17) | 1
27 | Nut M3 | 2
28 | Countersunk Screw M3x12 | 2

* metal rigid coupling can be used instead of 3D printed part ** flexible beam coupling is not recommended to use

Step 1.2 (assemble according to the drawing)
PART # | PART NAME | QTY
17 | Back Support | 1
27 | Nut M3 | 2
30 | Countersunk Screw M3x20 | 4

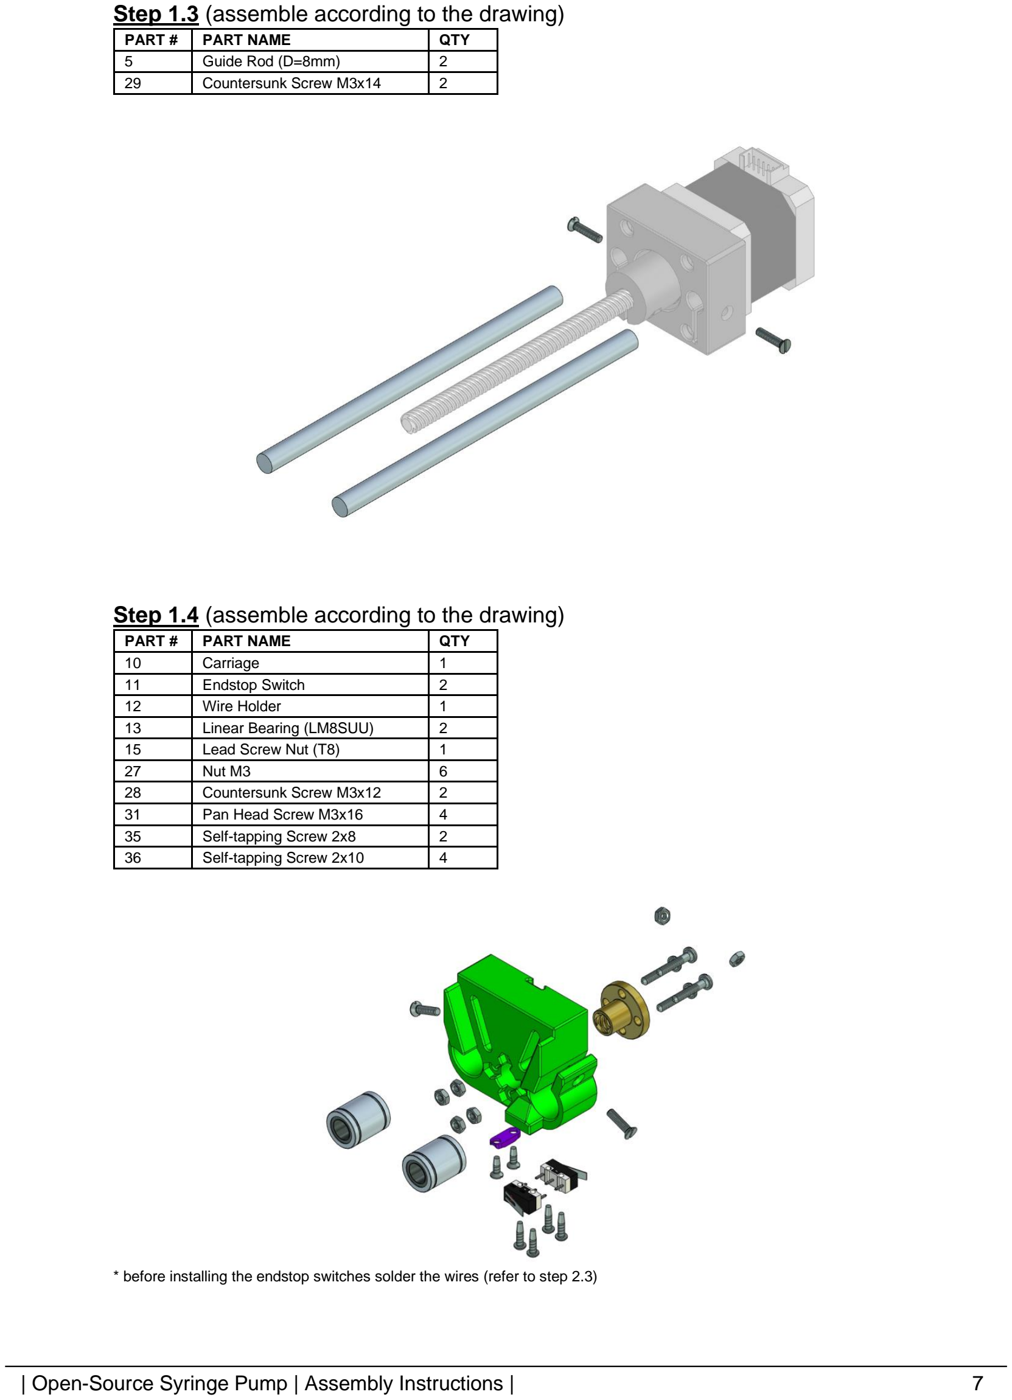
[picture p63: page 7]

Step 1.3 (assemble according to the drawing)
PART # | PART NAME | QTY
5 | Guide Rod (D=8mm) | 2
29 | Countersunk Screw M3x14 | 2
Step 1.4 (assemble according to the drawing)
PART # | PART NAME | QTY
10 | Carriage | 1
11 | Endstop Switch | 2
12 | Wire Holder | 1
13 | Linear Bearing (LM8SUU) | 2
15 | Lead Screw Nut (T8) | 1
27 | Nut M3 | 6
28 | Countersunk Screw M3x12 | 2
31 | Pan Head Screw M3x16 | 4
35 | Self-tapping Screw 2x8 | 2
36 | Self-tapping Screw 2x10 | 4

* before installing the endstop switches solder the wires (refer to step 2.3)

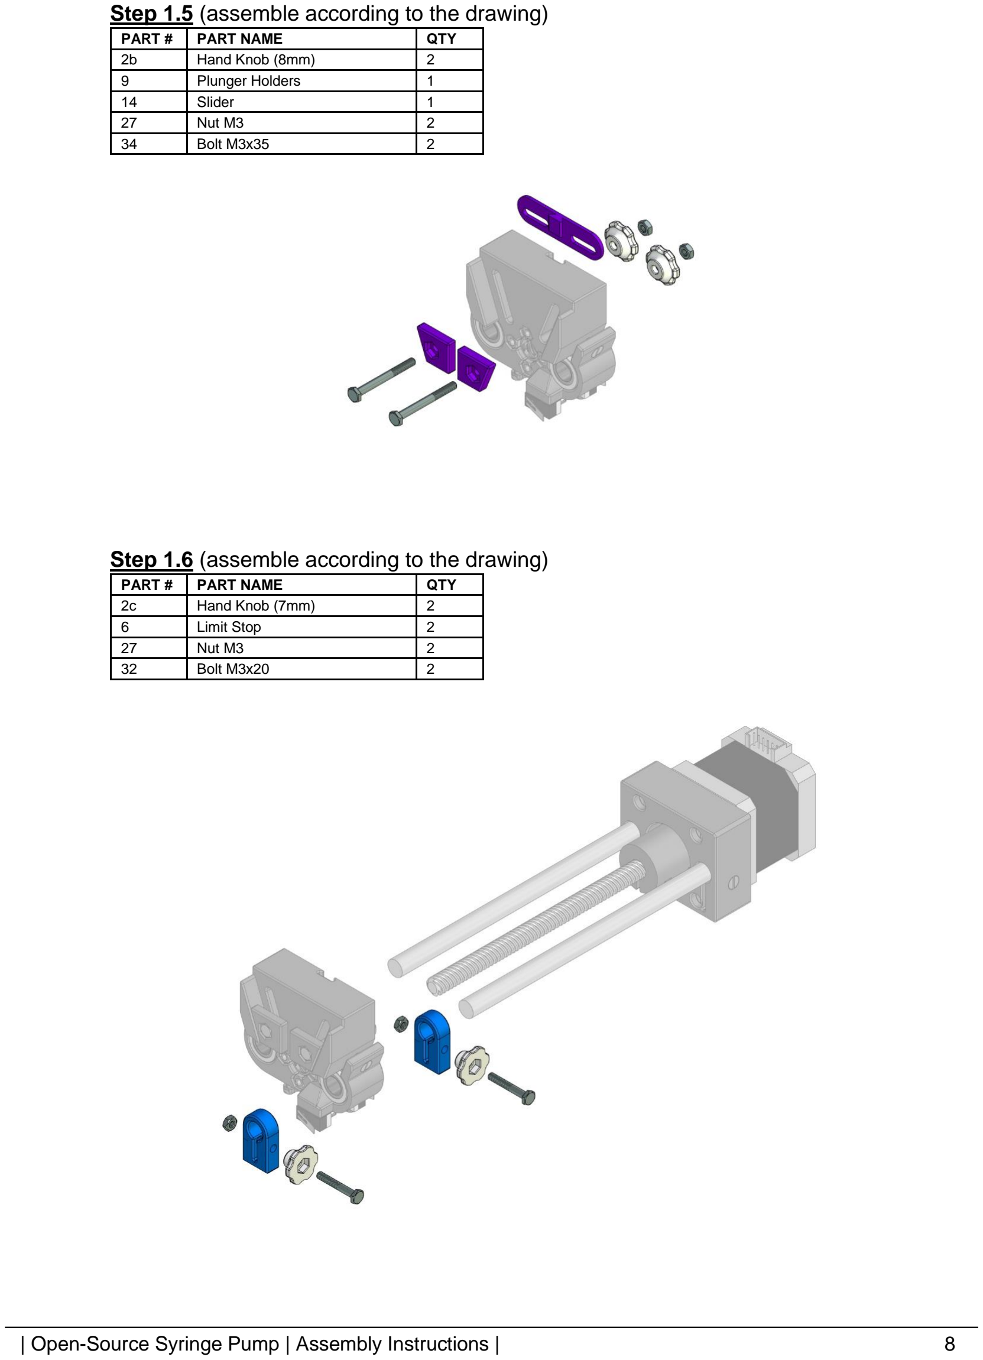
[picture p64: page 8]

Step 1.5 (assemble according to the drawing)
PART # | PART NAME | QTY
2b | Hand Knob (8mm) | 2
9 | Plunger Holders | 1
14 | Slider | 1
27 | Nut M3 | 2
34 | Bolt M3x35 | 2
Step 1.6 (assemble according to the drawing)
PART # | PART NAME | QTY
2c | Hand Knob (7mm) | 2
6 | Limit Stop | 2
27 | Nut M3 | 2
32 | Bolt M3x20 | 2

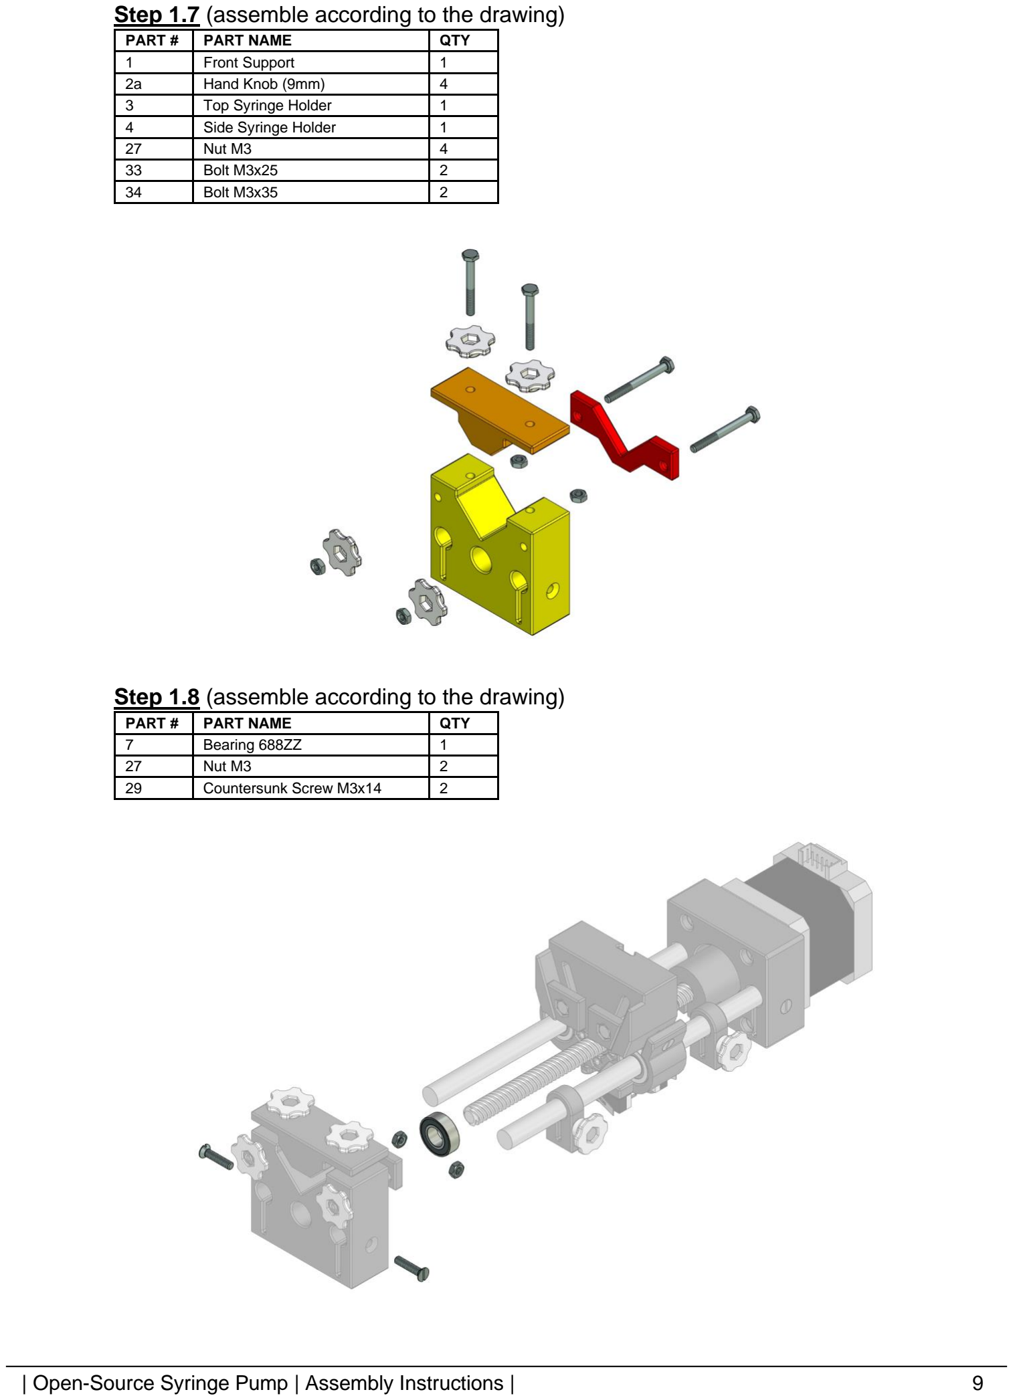
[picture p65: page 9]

Step 1.7 (assemble according to the drawing)
PART # | PART NAME | QTY
1 | Front Support | 1
2a | Hand Knob (9mm) | 4
3 | Top Syringe Holder | 1
4 | Side Syringe Holder | 1
27 | Nut M3 | 4
33 | Bolt M3x25 | 2
34 | Bolt M3x35 | 2
Step 1.8 (assemble according to the drawing)
PART # | PART NAME | QTY
7 | Bearing 688ZZ | 1
27 | Nut M3 | 2
29 | Countersunk Screw M3x14 | 2

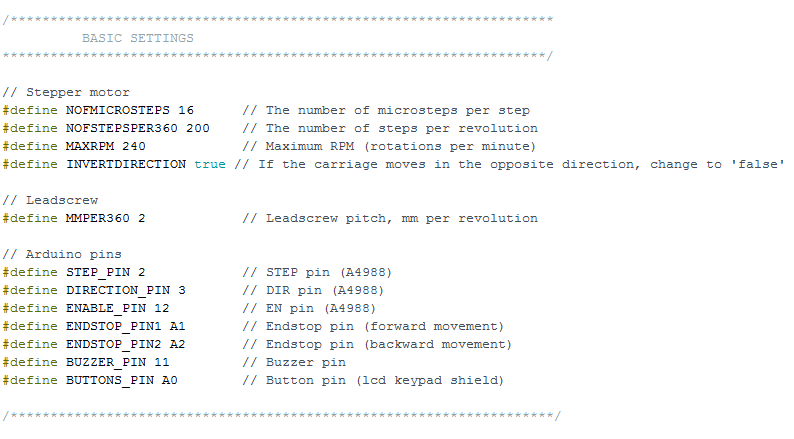
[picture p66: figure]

Step 2.1 (if necessary, change the basic settings in the Arduino sketch)
Step 2.2 (upload sketch to Arduino) Detailed instructions are available at this link. (https://www.arduino.cc/en/main/howto)
Step 2.3 (solder wires and crimp connectors, refer to electrical circuit)
PART # | PART NAME | QTY
22 | Arduino UNO | 1
26 | Active Buzzer (D=12mm) | 1
37 | Dupont Connector (Female) | 6
38 | Dupont Connector (Male) | 3
39 | Dupont Housing (3P) | 2
40 | Connector Wires | –

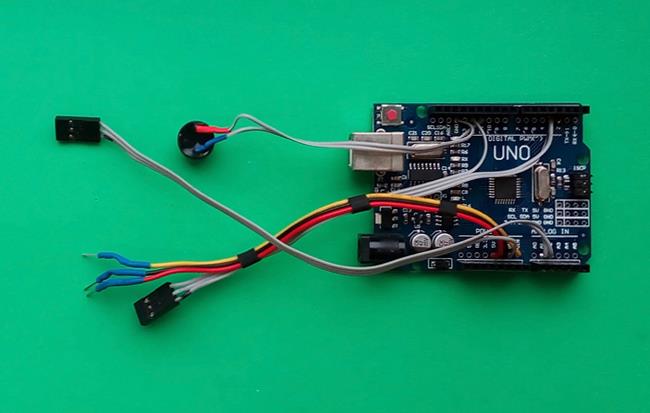
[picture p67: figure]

Step 2.4 (solder wires and crimp connectors, refer to electrical circuit)
PART # | PART NAME | QTY
11 | Endstop Switch | 2
38 | Dupont Connector (Male) | 3
39 | Dupont Housing (3P) | 1
40 | Connector Wires | –

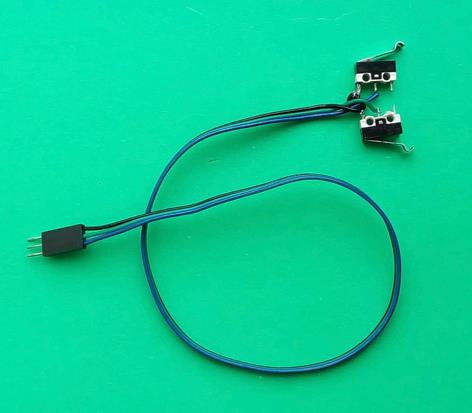
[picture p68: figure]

Step 2.5 (plug A4988 driver into the shield and set all DIP switches to ON)
PART # | PART NAME | QTY
24 | Stepper Motor Driver (A4988) | 1
25 | Control Shield for A4988 | 1

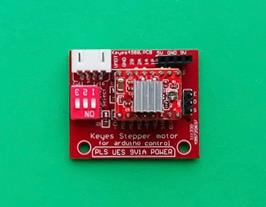
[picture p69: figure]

Step 2.6 (set output current limit on A4988) Detailed instructions are available at this link. (https://howtomechatronics.com/tutorials/arduino/how-to-control-stepper-motor-with-a4988-driver-and-arduino/)

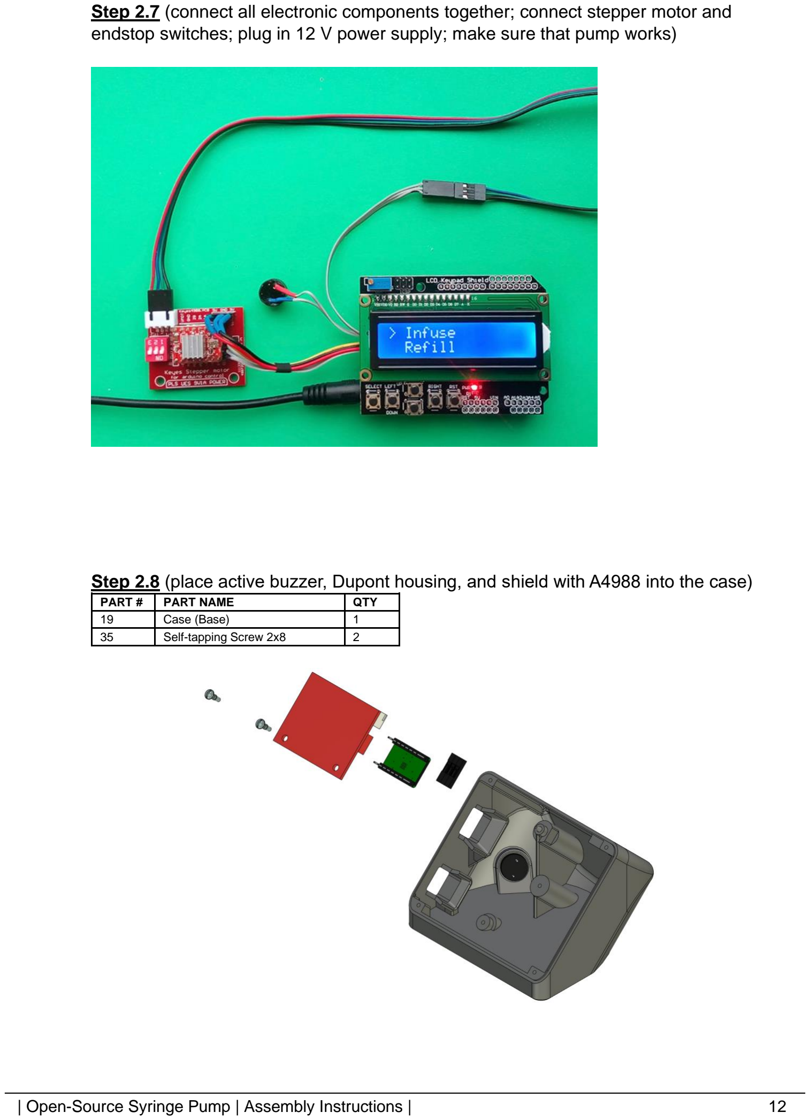
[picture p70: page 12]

Step 2.7 (connect all electronic components together; connect stepper motor and endstop switches; plug in 12 V power supply; make sure that pump works)
Step 2.8 (place active buzzer, Dupont housing, and shield with A4988 into the case)
PART # | PART NAME | QTY
19 | Case (Base) | 1
35 | Self-tapping Screw 2x8 | 2

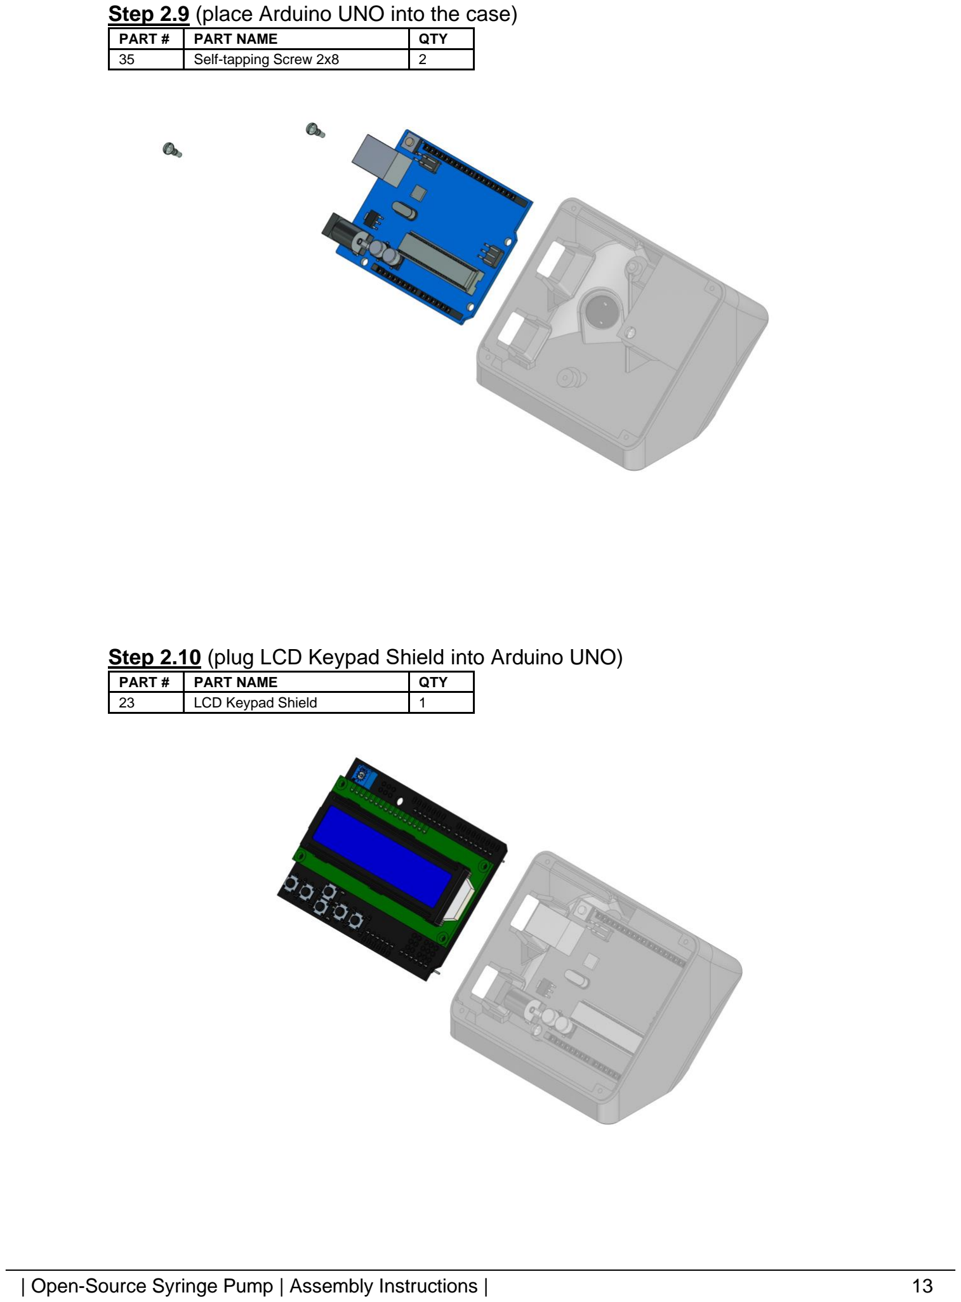
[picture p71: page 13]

Step 2.9 (place Arduino UNO into the case)
PART # | PART NAME | QTY
35 | Self-tapping Screw 2x8 | 2
Step 2.10 (plug LCD Keypad Shield into Arduino UNO)
PART # | PART NAME | QTY
23 | LCD Keypad Shield | 1

Step 2.11 (install buttons and top cover)
PART # | PART NAME | QTY
20 | Case (Cover) | 1
21 | Buttons | 1
36 | Self-tapping Screw 2x10 | 4

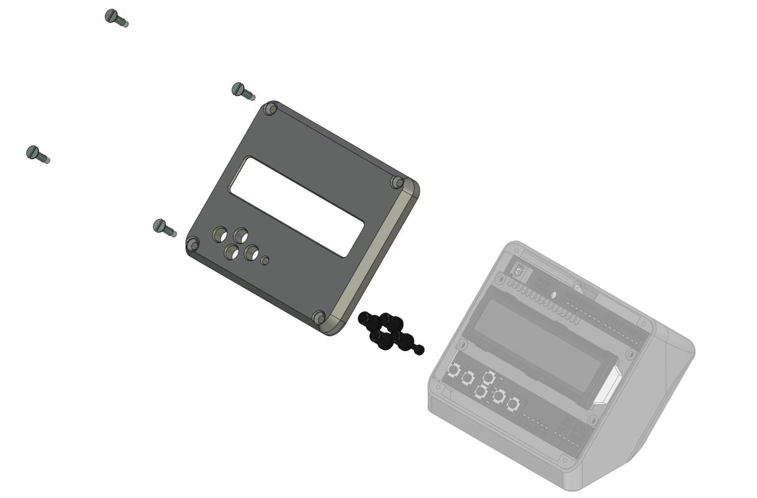
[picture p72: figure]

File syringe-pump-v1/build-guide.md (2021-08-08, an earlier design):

# Syringe Pump v1 - Based on the OSSP

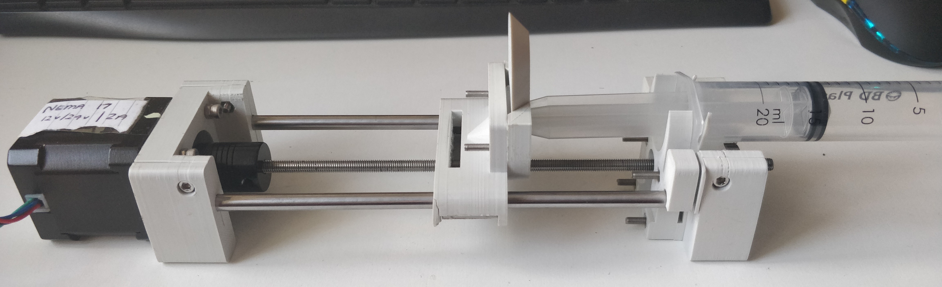
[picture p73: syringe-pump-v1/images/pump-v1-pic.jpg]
Pump v1 Image


---
## Build Guide

The original build guide found [here](https://www.appropedia.org/Open-source_syringe_pump#How_to_Build_an_Open-source_Syringe_Pump) isn't very clear on certain instructions, so I improved upon them to make the build process
easier for anyone who wants to replicate the design. The printable STL files also include my modified versions of the original carriage and syringe holders which makes building and operating the pump easier.

---
## Parts List

### Tools

* 2mm Allen Key
* 3mm Allen Key

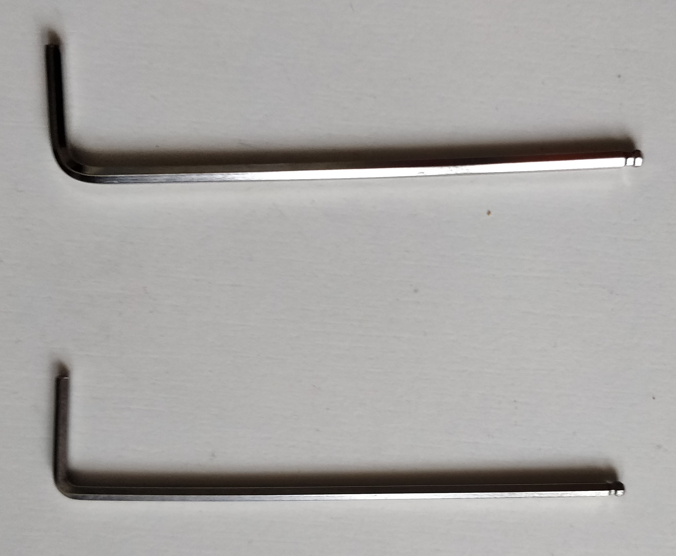
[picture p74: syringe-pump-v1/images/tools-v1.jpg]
Tools Image


### 3D Printed Parts

* [Motor End](./stl-files/motor-end.stl)
* [Carriage (modified)](./stl-files/carriage-modified.stl)
* [Plunger Holder Base](./stl-files/plunger-holder-base-and-tab.stl)
* [Plunger Holder Tab](./stl-files/plunger-holder-base-and-tab.stl)
* [Idler End](./stl-files/idler-end.stl)
* [Syringe Body Holder (modified) (x2)](./stl-files/syringe-holder-modified.stl)

### Bill of Materials

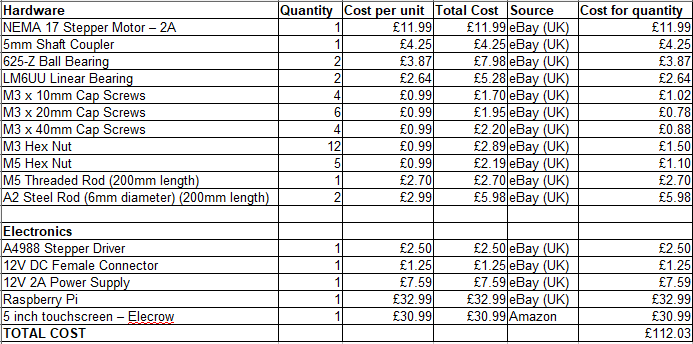
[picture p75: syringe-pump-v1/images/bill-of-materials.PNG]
Bill of Materials Spreadsheet


### Exploded Parts View

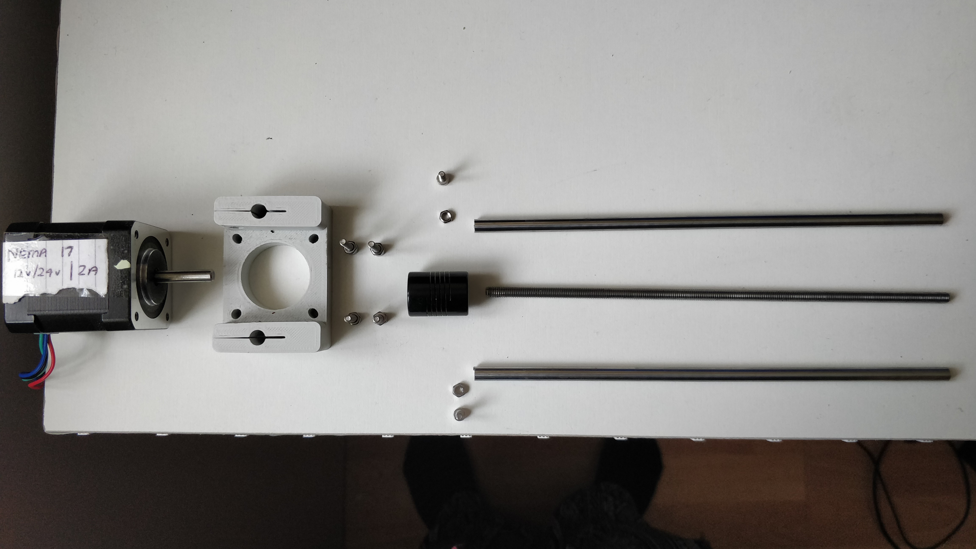
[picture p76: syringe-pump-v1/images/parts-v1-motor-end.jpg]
Parts view of Motor End

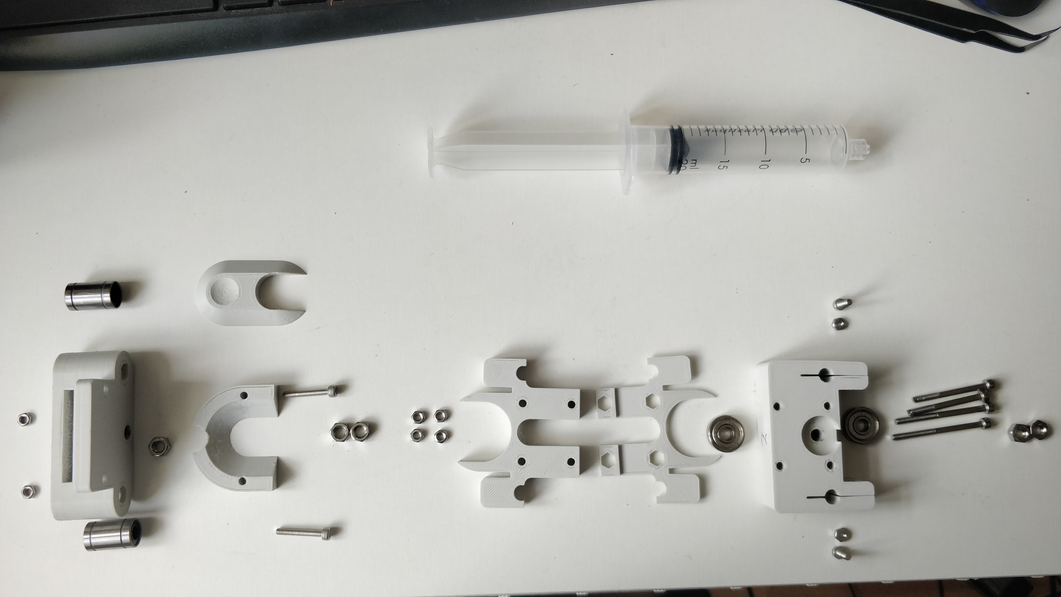
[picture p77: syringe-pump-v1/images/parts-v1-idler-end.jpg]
Parts view of Idler End


---
## Build Steps

1. Insert 2 M3 hex nuts into the inside of the Motor End

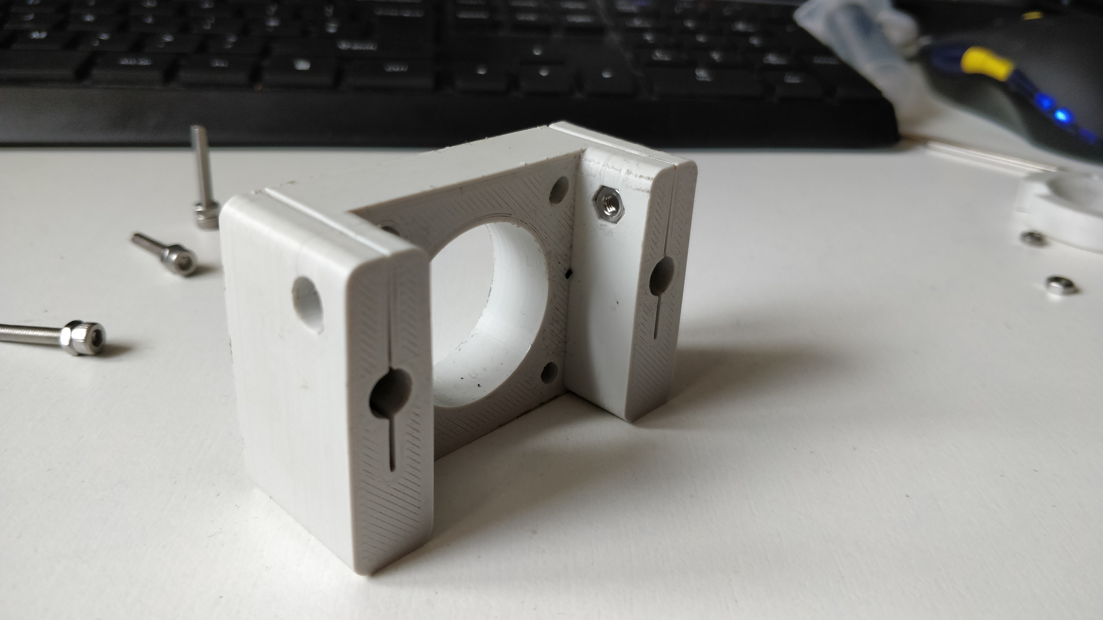
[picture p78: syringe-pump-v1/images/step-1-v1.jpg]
Step 1 Image


2. Using 4 M3 x 20mm cap screws and 4 M3 hex nuts, attach the Motor End to the NEMA 17 Stepper Motor
   (NOTE: The nuts go on the inside of the Motor End for spacing and to help reduce vibrations)

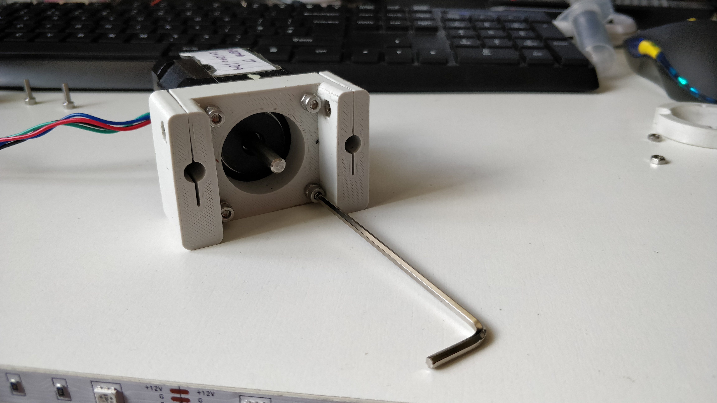
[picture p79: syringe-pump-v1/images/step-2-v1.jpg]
Step 2 Image


3. Attach the 2 steel rods into the holes in the Motor End and secure them with 2 M3 x 10mm screws

Step 3 Image

4. Loosen the 4 screws on the coupler, insert the threaded rod half way into the coupler and tighten
   the 2 coupler screws on the threaded rods side

Step 4 Image

5. Insert the coupler into the NEMA 17 motor and tighten the last 2 screws on the coupler

Step 5 Image

6. Insert the 2 linear bearings into each side of the Carriage and push an M5 hex nut into the bottom of
   the Carriage
   (NOTE: For the unmodified Carriage you will need to cut out spaces for the linear bearings)

Step 6 Image

7. Attach the Plunger Holder Base to the Carriage using 2 M3 hex nuts and 2 M3 x 20mm cap screws

Step 7 Image

8. Slide the carriage onto the threaded rod and steel rods ensuring they go through the bearings and M5 hex nut,
   twisting the coupler counter-clockwise to slide the carriage halfway down the rods

Step 8 Image

9. Twist 2 M5 hex nuts onto the threaded rod leaving a gap between them and the carriage

Step 9 Image

10. Insert 2 M3 hex nuts and the 2 ball bearings into the Idler End and slide it onto the rods

Step 10 Image

11. Twist 2 M5 hex nuts onto the end of the threaded rod up to the ball bearing on the outside of the
    Idler End and twist the 2 M5 hex nuts from step 9 up to the ball bearing on the other side

Step 11 Image

12. Tighten the steel rods to the Idler End using 2 M3 x 10mm cap screws

Step 12 Image

13. Line up the 2 Syringe Body Holders from the Idler End and place the syringe between them with the
    bumped side facing towards the Motor End

Step 13 Image

14. Using 4 M3 hex nuts on the Body Holder closest to the carriage and 4 M3 x 40mm cap screws on the Idler
    End screw the Body Holders together onto the Idler End, ensuring the Syringe Body is tight in the
    Plunger Holder with the tab and between the 2 Body Holders

Step 14 Image

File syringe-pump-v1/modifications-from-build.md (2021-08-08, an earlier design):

# Modification Ideas From Build

After following the build instructions from the OSSPL [1] I realised that:

* Some steps were not descriptive enough
* The Bill of Materials had some wrong quantities
* What 3D printed parts need changes to improve the build process

## List of Modifications

### Carriage (Part #4)

* Modify openSCAD file to print spacing for the 2 linear bearings to fit without having to cut
into either side of the carriage - isn't easy and is also dangerous

* Allow spacing all the way through the 3 rod holes so the builder doesn't have to cut these out
themselves

### Plunger Holder (Part #7)

* Modify this to be wider and taller to fit up to a 60mL syringe - take measurements from 20mL and
60mL syringe plungers so all sizes inclusive will fit

### Body Holders (Part #5)

Currently can think of 2 options for changing this:

* Make an adjustable body holder made for a 60mL syringe, with a fitting for smaller sizes to stop
the syringe moving around

* Modify the openSCAD file to make multiple body holders that can be swapped out once syringe sizes
change

### Extra Points

* Used 4 extra M3 hex nuts for spacing between the motor end and the M3x20mm cap screws holding the
motor in place

* Replaced 2x M3x10mm cap screws with M3x20mm cap screws for attaching the carriage to the plunger holder - 10mm screws were not long enough to hold them together

## References
[1] https://www.appropedia.org/Open-source_syringe_pump#How_to_Build_an_Open-source_Syringe_Pump

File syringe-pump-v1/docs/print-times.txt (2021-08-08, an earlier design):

linear-actuator-v0-1 : 4h7m
linear-actuator-v0-2 : 4h
linear-actuator-v0-3 : 2h33m
linear-actuator-v0-4 : 3h10m
linear-actuator-v0-5 : 1h52m
linear-actuator-v0-6 : 40m
linear-actuator-v0-7 : 1h23m
linear-actuator-v0-8 : 29m

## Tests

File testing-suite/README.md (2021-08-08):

# Pump Testing Suite

The files here contain functions that test the operation of the stepper motors,
limit switches and the lookup tables I calculated to define the number of steps
it takes to infuse a set size BD PlastiPak syringe at a given micro-stepping rate.

---
<b> NOTE: </b> These functions are written in Python 3.x.x and require the `RPi.GPIO` library to run.

## `pump-test.py`

### Tests for Syringe Pump v1

#### Variables

```
DIR = 20         # sets revolution direction
STEP = 21        # activates the stepper motor
CW = 1           # identifier for clockwise
CCw = 0          # identifier for anticlockwise
MODE = (5,6,13)  # setting micro-step resolution

FRONT_SW = 16    # detect front limit switch is pressed
BACK_SW = 19     # detect back limit switch is pressed

RESOLUTION = {'1':(0,0,0),  # signal map for micro-step resolutions
            '1/2':(1,0,0),
            '1/4':(0,1,0),
            '1/8':(1,1,0),
            '1/16':(1,1,1)}

STEPS = {'1':200,           # steps per revolution for each resolution level
         '1/2':400,
         '1/4':800,
         '1/8':1600,
         '1/16':3200}

DELAY = {'1':0.003,         # map of delay times for testing purposes
         '1/2':0.005/4,
         '1/4':0.005/4,
         '1/8':0.005/4,
         '1/16':0.005/4}

MS = ['1','1/2','1/4','1/8','1/16'] # list of micro-step resolutions

```
#### Methods
---
`def setup()`

Warnings are disabled due to the `STEP` and `DIR` pins being reinitialised.

Then we setup our output pins: `STEP`, `DIR` and `MODE`.

Finally we setup our input pins: `FRONT_SW` and `BACK_SW`.

---
`def revolution(dir, res)`

Given a direction `dir={0|1}` and a micro-step resolution `res={'1'|'1/2'|'1/4'|'1/8'|'1/16'}` it will
complete a single revolution with the number of steps required by the given resolution string.

---
`def all_microsteps(dir)`

For every possible micro-step resolution defined in the list `MS` perform one revolution of
the stepper motor.

---
`def test_1()`

Runs 50 revolutions with a micro-step resolution of `'1'`.

Then runs 30 revolutions with a micro-step resolution of `'1/4'`.

---
`def set_microstep(ms)`

Sets the output pins in `MODE` to the given resolution `ms` as a string mapped in the dictionary
`RESOLUTION`.

---
`def set_direction(dir)`

Sets the `DIR` pin to the identifier passed as `dir={CW|CCW}`.

---
`def withdraw_continuous()`

Sets direction to `CCW` and micro-step resolution to `'1'` and runs the stepper motor
indefinitely.

---
`def infuse_continuous()`

Sets direction to `CW` and micro-step resolution to `'1'` and runs the stepper motor
indefinitely.

### Tests for Syringe Pump v2

#### Variables

```
# micro-step resolution -> step : maps for syringe pump v1

# steps for infusing/withdrawing the entire 20ml syringe
ms_to_steps_20 = {'1':17500, '1/2':35000, '1/4':70000, '1/8':140000, '1/16':280000}

# steps for infusing/withdrawing the entire 60ml syringe
ms_to_steps_60 = {'1':27250, '1/2':54500, '1/4':109000, '1/8':218000, '1/16':436000}

# combine the above dictionaries into one dictionary

ms_size_steps = {20:{'1':17500, '1/2':35000, '1/4':70000, '1/8':140000, '1/16':280000},
                 60:{'1':27250, '1/2':54500, '1/4':109000, '1/8':218000, '1/16':436000}}

# micro-step resolution -> step : maps for syringe pump v2

v2_ms_size_steps = {20:{'1':7000, '1/2':14000, '1/4':28000, '1/8':56000, '1/16':112000},
                    60:{'1':10900, '1/2':21800, '1/4':43600, '1/8':87200, '1/16':174400}}
```

#### Methods
---
`def calculate_delay(ms, infuse_time, syringe_size)`

Using the `ms_to_steps_20` and `ms_to_steps_60` dictionaries, based on the given `syringe_size`
we get the total number of steps to infuse the syringe at the given `ms`.

Then we calculate the delay with `delay = total_steps/infuse_time` and return it.

---
`def pump(dir, ms, infuse_time, syringe_size)`

Uses `set_microstep(ms)` and `set_direction(dir)` to initialise the outputs.

Then calculated the delay using `calculate_delay(ms, infuse_time, syringe_size)`.

Finally it gets the total number of steps required using `syringe_size` and runs the pump, delaying
each step using the delay value calculated.

---
`def test_2()`

Runs the function `pump(CW, '1/2', 60, 20)`

---
`def infuse_continuous_switch()`

Uses `set_microstep('1')` and `set_direction(CW)` to initialise the outputs.

Then it starts a loop to operate the pump until a signal is detected on the front limit switch
using `GPIO.input(FRONT_SW)`

---
`def withdraw_continuous_switch()`

Uses `set_microstep('1')` and `set_direction(CCW)` to initialise the outputs.

Then it starts a loop to operate the pump until a signal is detected on the back limit switch
using `GPIO.input(BACK_SW)`.

This switch will be activated by a stopper that sits on one of the rails of the pump.

---

## `Pumpy.py`

Initial version of the `Pumpy` class that encapsulates all the behaviour of the functions written
in `pump-test.py` into a single object that can be easily instantiated and run.

The dictionaries `MS_SIZE_STEPS_V1` and `MS_SIZE_STEPS_V2` are lookup tables calculated using the
formulea described [here](./pump-maths.md).

### Class Variables

```
INFUSE = 1                          # CW
WITHDRAW = 0                        # CCW

MS_RESOLUTION = {"1": (0,0,0),      # Micro-stepping resolution mapping
               "1/2": (1,0,0),
               "1/4": (0,1,0),
               "1/8": (1,1,0),
               "1/16": (1,1,1)}

# lookup table for number of steps required to fully infuse one of 2 sizes of syringe
# at a chosen micro-step resolution, with a table for each pump version

MS_SIZE_STEPS_V1 = {20:{"1":17500, "1/2":35000, "1/4":70000, "1/8":140000, "1/16":280000},
                    60:{"1":27250, "1/2":54500, "1/4":109000, "1/8":218000, "1/16":436000}}

MS_SIZE_STEPS_V2 = {20:{'1':7000, '1/2':14000, '1/4':28000, '1/8':56000, '1/16':112000},
                    60:{'1':10900, '1/2':21800, '1/4':43600, '1/8':87200, '1/16':174400}}

# DEFINED IN CONSTRUCTOR

self.direction_pin           # output pin for setting direction
self.step_pin                # output pin for moving motor
self.mode = (ms1,ms2,ms3)    # output pin for setting micro-step resolution
self.spr = spr               # default steps per revolution for the motor
self.f_switch = f_switch     # input pin for front limit switch
self.b_switch = b_switch     # input pin for back limit switch

```
---
`def __init__(self, dir, step, ms1, ms2, ms3, f_switch, b_switch, spr=200)`

Constructor for Pumpy class with input and output pin parameters and a default steps per revolution
value - the NEMA 17 motor in use has a default steps per revolution of 200.

---
`def setup(self)`

Basic GPIO setup functions to disable warnings (direction and step pins get reinitialised on each operation),
set the pin description mode to BCM (Broadcom) and setting the pin input and outputs.

---
`def set_microstep(self, ms)`

Sets the pins of `self.mode` to the micro-step resolution given by `ms` - the key in the dictionary
`MS_RESOLUTION`.

---
`def set_direction(self, dir)`

Sets the `self.direction_pin` output pin to an integer variable, either `INFUSE` or `WITHDRAW`.
Their values as integers are 1 and 0 respectively.

---
`def continuous(self, dir)`

Sets the `self.direction_pin` output pin to `dir`, sets the micro-step resolution to `'1'`, sets up
which limit switch will be activated using `dir` and runs the motor until the limit switch input is
activated

---
`def stop(self)`

Sets the `self.step_pin` output to `GPIO.LOW` - it is used to stop any operation of the pump.

---
`def calculate_delay(self, infuse_time, syringe_size, ms)`

Based on the given `syringe_size` and `ms` it finds the total number of steps required to infuse
the syringe as `self.MS_SIZE_STEPS_V(1/2)[syringe_size][ms]`. This value is divided by `infuse_time` to
give the delay required per step

---
`def pump(self, dir, infuse_time, syringe_size, ms)`

Uses `set_direction(self, dir)` and `set_microstep(self, ms)` to set the correct outputs and calculates the
delay per step using `calculate_delay(self, infusion_time, syringe_size, ms)`.

Finally it gets the total number of steps from `self.MS_SIZE_STEPS_V(1/2)[syringe_size][ms]` and runs the motor
for that many steps, delaying between each pin output call.

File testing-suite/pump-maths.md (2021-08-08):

# Syringe Pump Maths Calculations

## Variables

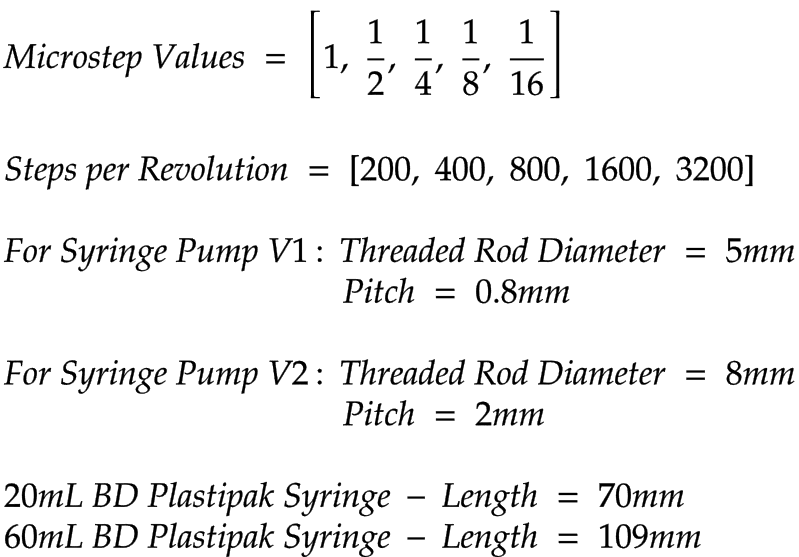
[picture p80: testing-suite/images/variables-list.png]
Variables List


## Formulea

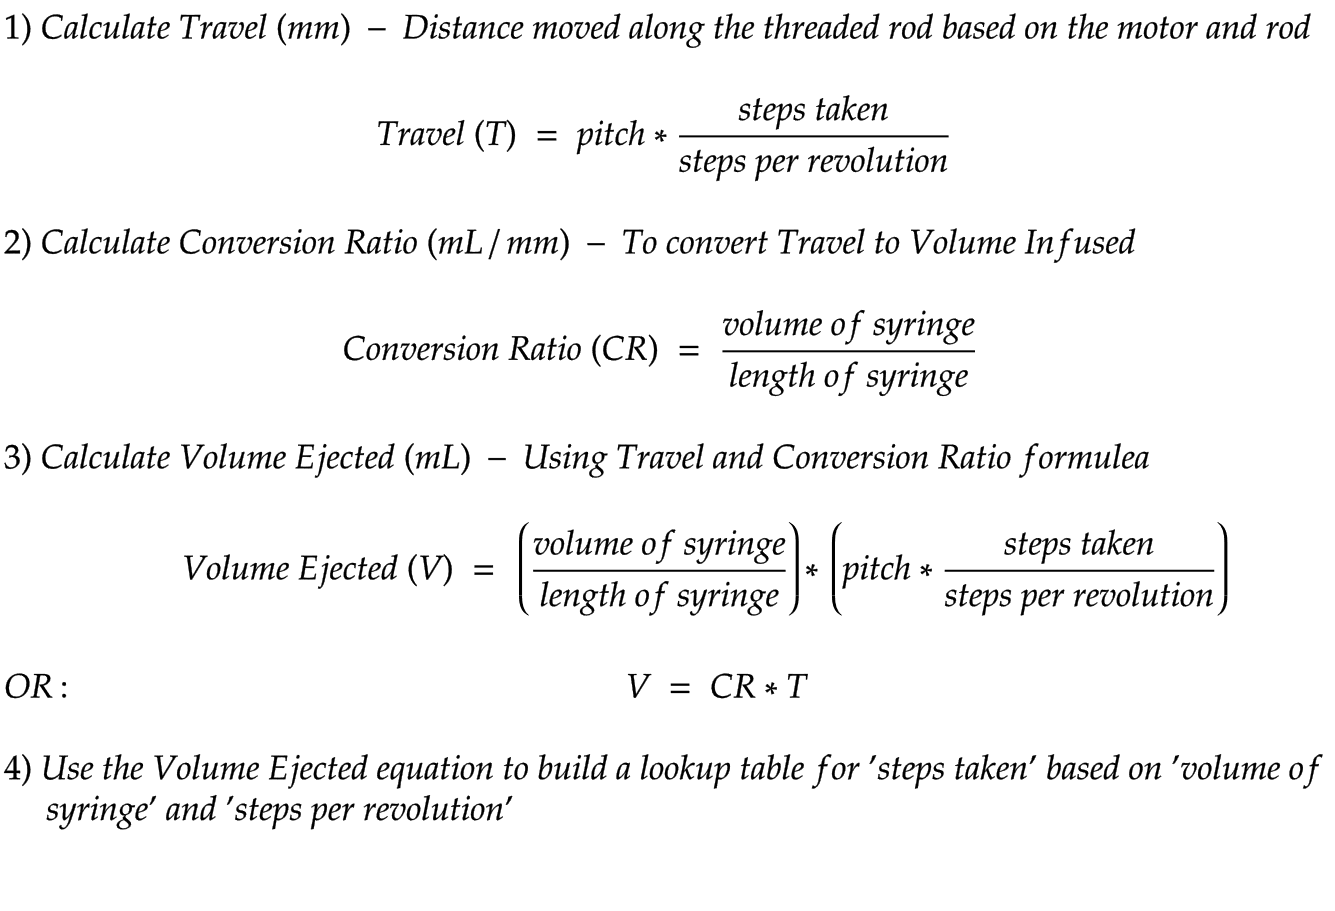
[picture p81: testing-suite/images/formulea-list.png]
Formulea List


## Syringe Pump v1 Lookup Table

| Steps per Revolution | Microstepping Value | 20mL    | 60mL    |
|----------------------|---------------------|---------|---------|
| 200                  | 1                   | 17,500  | 27,250  |
| 400                  | 1/2                 | 35,000  | 54,500  |
| 800                  | 1/4                 | 70,000  | 109,000 |
| 1600                 | 1/8                 | 140,000 | 218,000 |
| 3200                 | 1/16                | 280,000 | 436,000 |

## Syringe Pump v2 Lookup Table

| Steps per Revolution | Microstepping Value | 20mL    | 60mL    |
|----------------------|---------------------|---------|---------|
| 200                  | 1                   | 7000    | 10,900  |
| 400                  | 1/2                 | 14,000  | 21,800  |
| 800                  | 1/4                 | 28,000  | 43,600  |
| 1600                 | 1/8                 | 56,000  | 87,200  |
| 3200                 | 1/16                | 112,000 | 174,400 |

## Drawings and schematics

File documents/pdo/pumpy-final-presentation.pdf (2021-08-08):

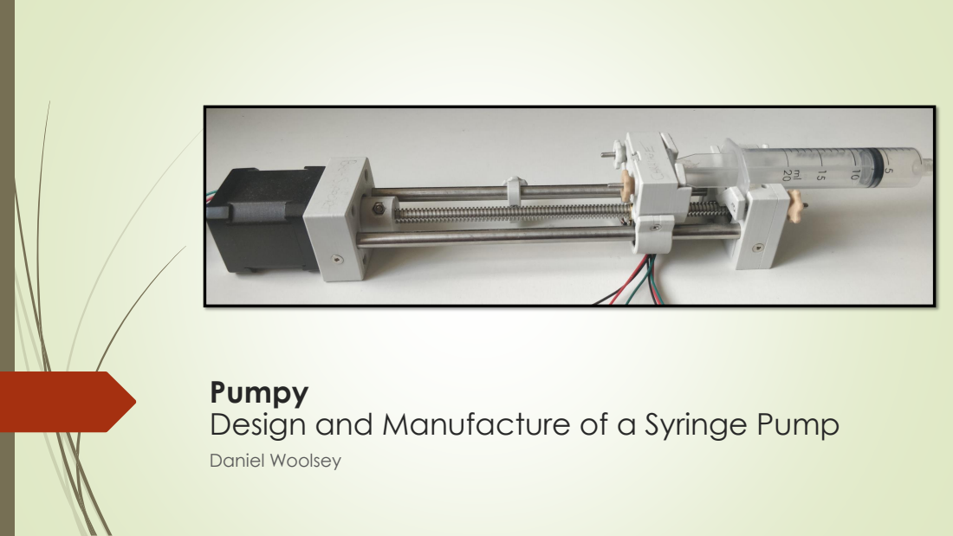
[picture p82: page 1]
Daniel Woolsey

Pumpy
Design and Manufacture of a Syringe Pump

# Contents

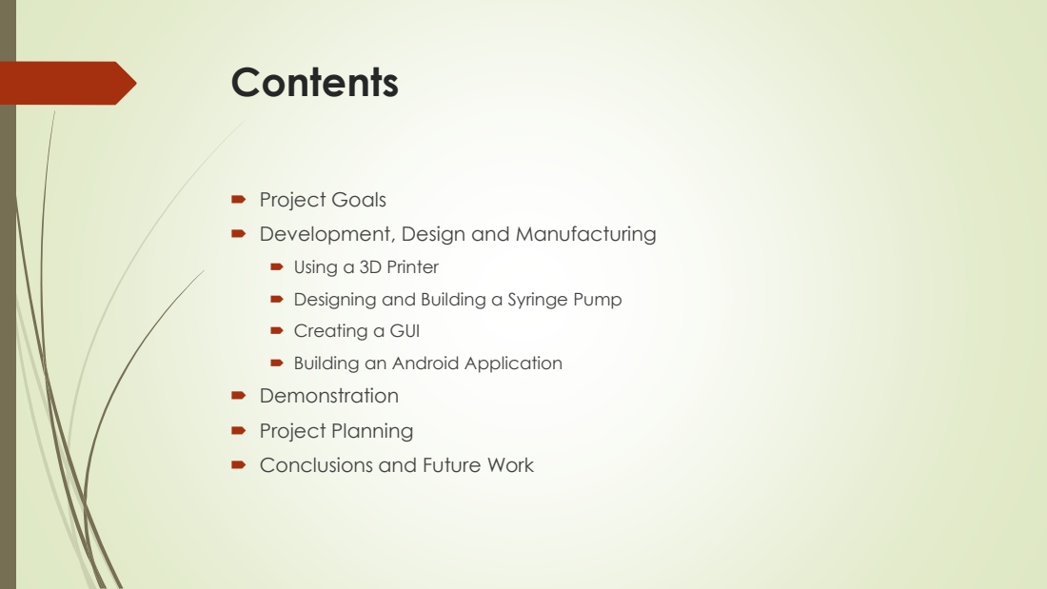
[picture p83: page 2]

Project Goals
Development, Design and Manufacturing

Using a 3D Printer
Designing and Building a Syringe Pump
Creating a GUI
Building an Android Application
Demonstration
Project Planning
Conclusions and Future Work

# Project Goals

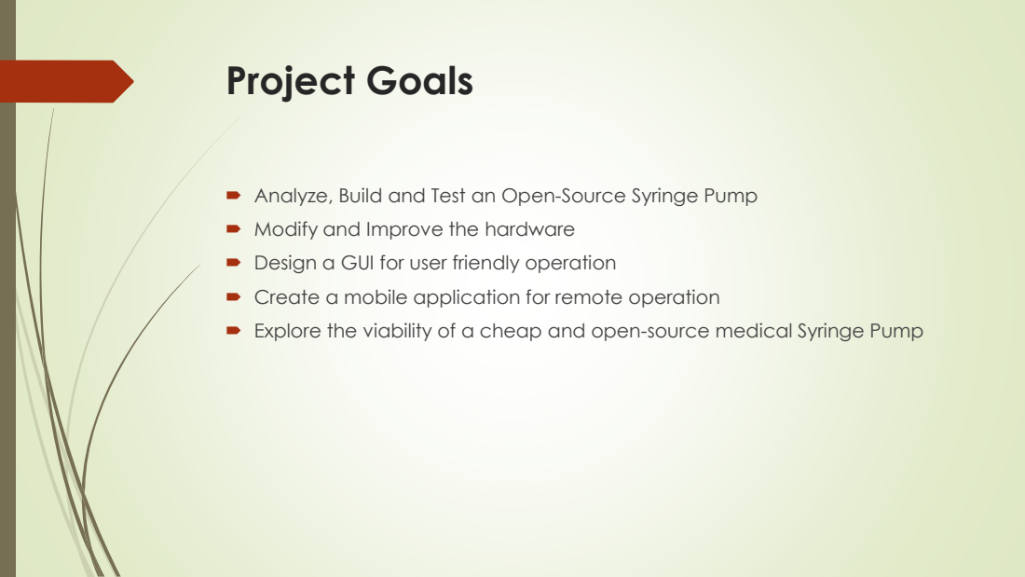
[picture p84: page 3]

Analyze, Build and Test an Open-Source Syringe Pump
Modify and Improve the hardware
Design a GUI for user friendly operation
Create a mobile application for remote operation
Explore the viability of a cheap and open-source medical Syringe Pump

# Development, Design and Manufacturing Using a 3D Printer

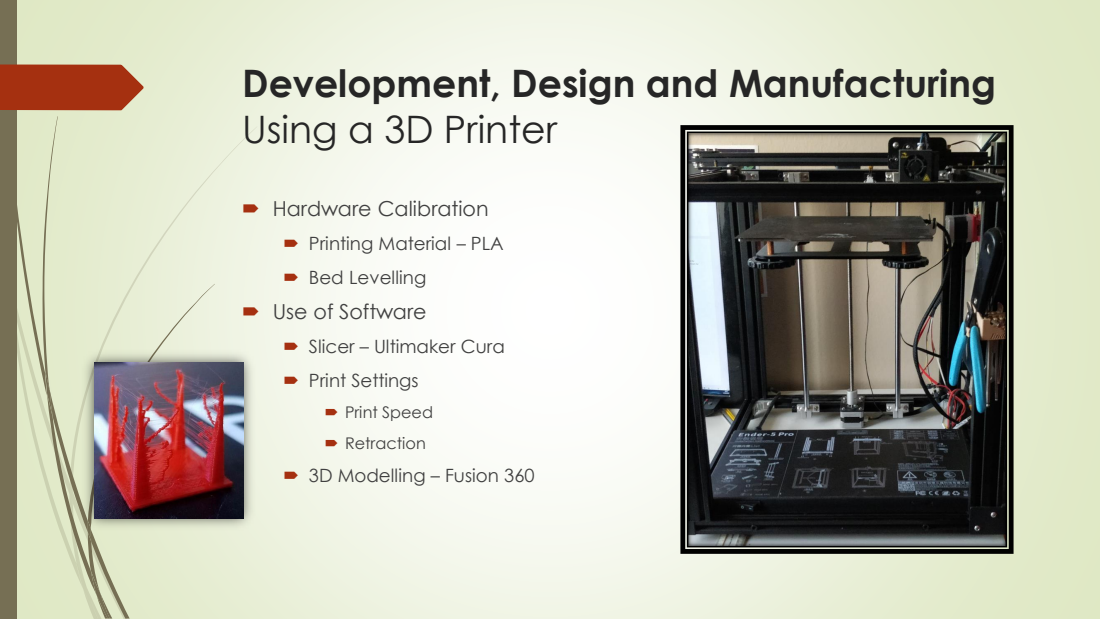
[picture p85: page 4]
Hardware Calibration; Print Speed; Retraction; 3D Modelling – Fusion 360

Printing Material – PLA
Bed Levelling
Use of Software

Slicer – Ultimaker Cura
Print Settings

## Development, Design and Manufacturing Designing and Building a Syringe Pump

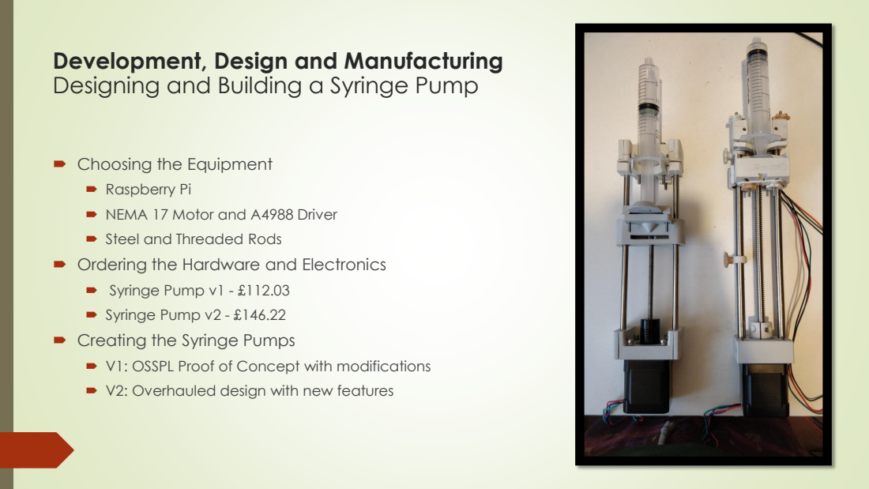
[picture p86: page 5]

Choosing the Equipment
Raspberry Pi
NEMA 17 Motor and A4988 Driver
Steel and Threaded Rods
Ordering the Hardware and Electronics
Syringe Pump v1 - £112.03
Syringe Pump v2 - £146.22
Creating the Syringe Pumps
V1: OSSPL Proof of Concept with modifications
V2: Overhauled design with new features

## Development, Design and Manufacturing

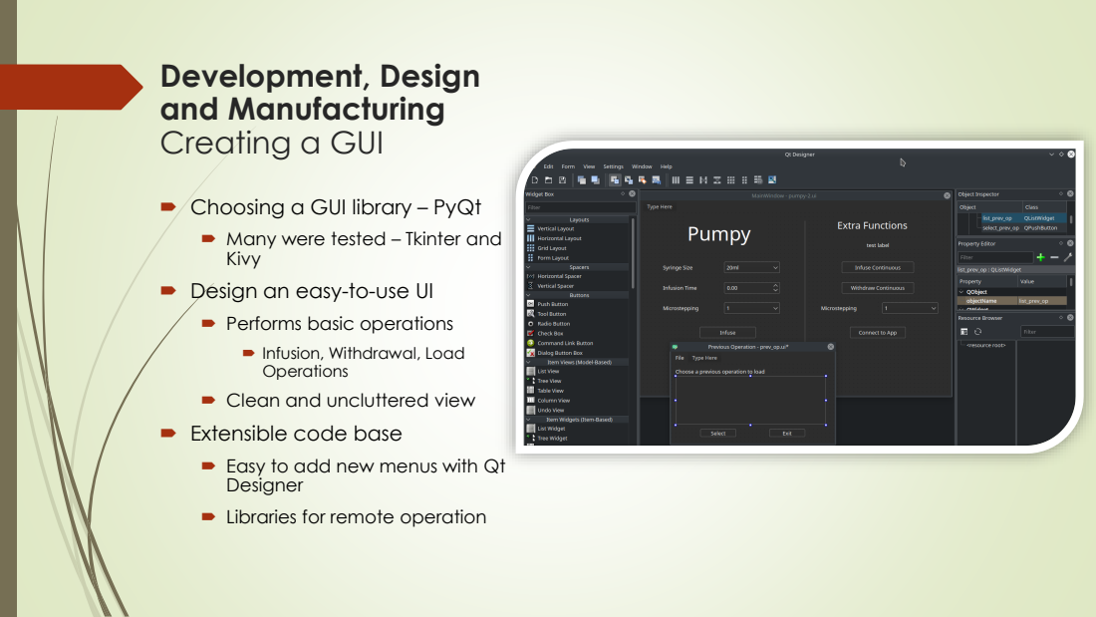
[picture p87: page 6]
Creating a GUI

Choosing a GUI library – PyQt
Many were tested – Tkinter and
Kivy

Design an easy-to-use UI
Performs basic operations

Infusion, Withdrawal, Load
Operations

Clean and uncluttered view
Extensible code base
Easy to add new menus with Qt
Designer
Libraries for remote operation

## Development, Design and Manufacturing

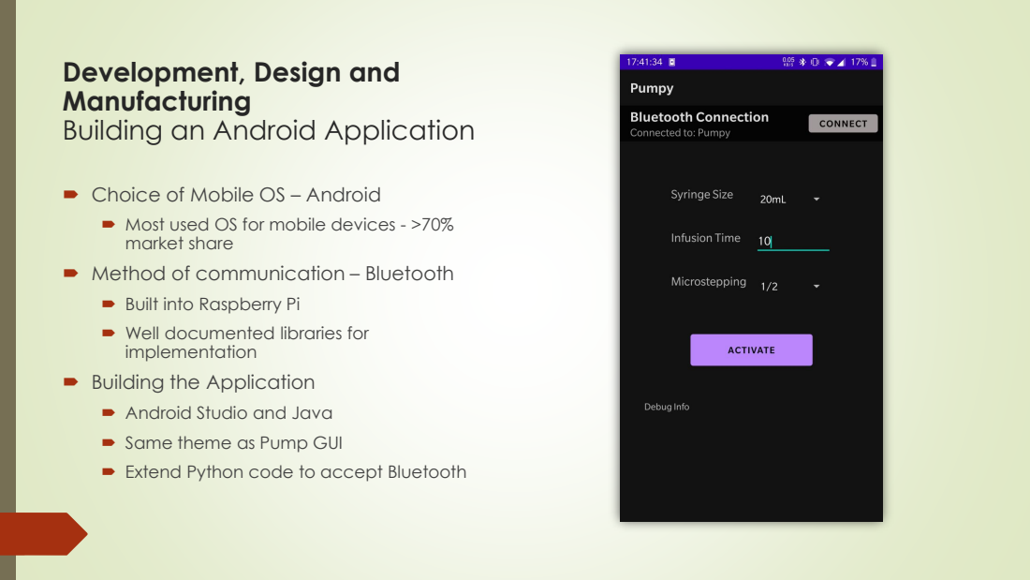
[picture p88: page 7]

Building an Android Application

Choice of Mobile OS – Android
Most used OS for mobile devices - >70%
market share

Method of communication – Bluetooth
Built into Raspberry Pi
Well documented libraries for
implementation

Building the Application
Android Studio and Java
Same theme as Pump GUI
Extend Python code to accept Bluetooth

# Demonstration

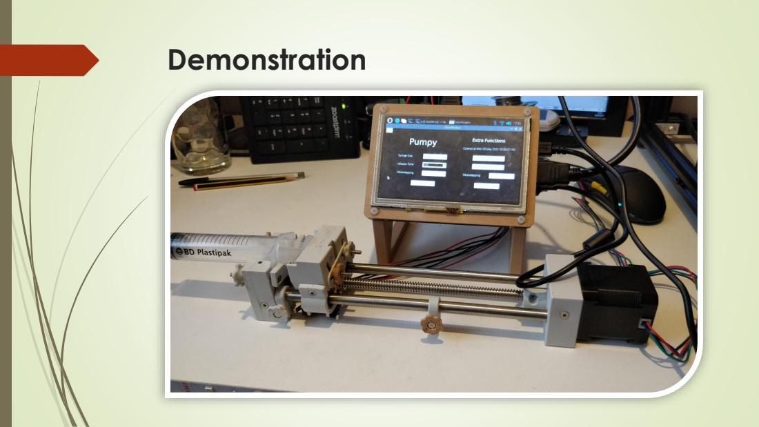
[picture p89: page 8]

# Project Planning

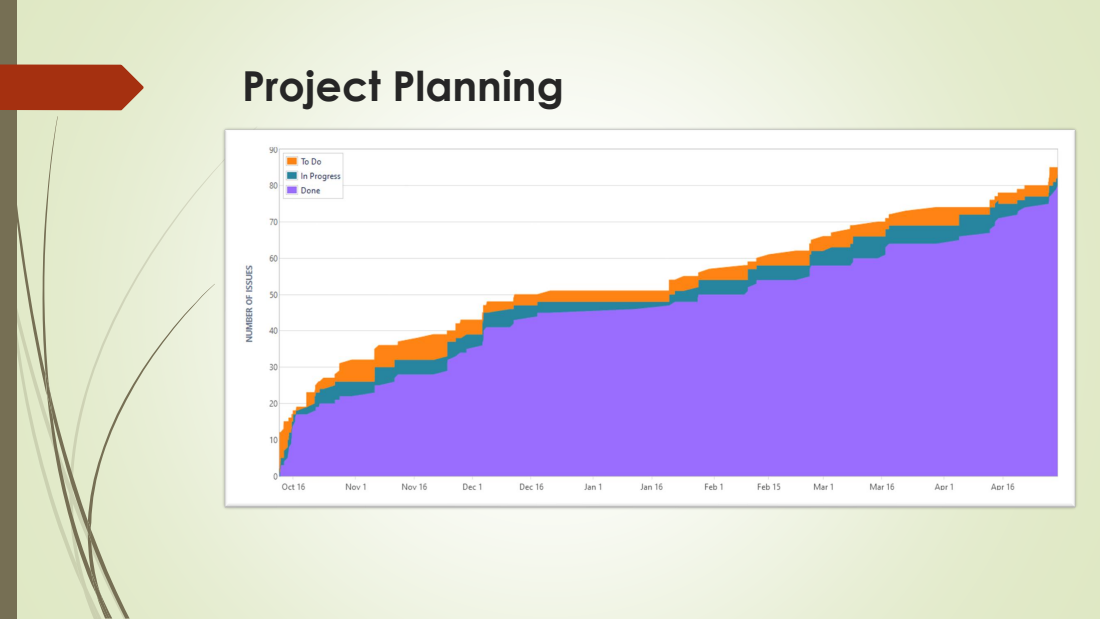
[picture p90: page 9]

# Project Planning

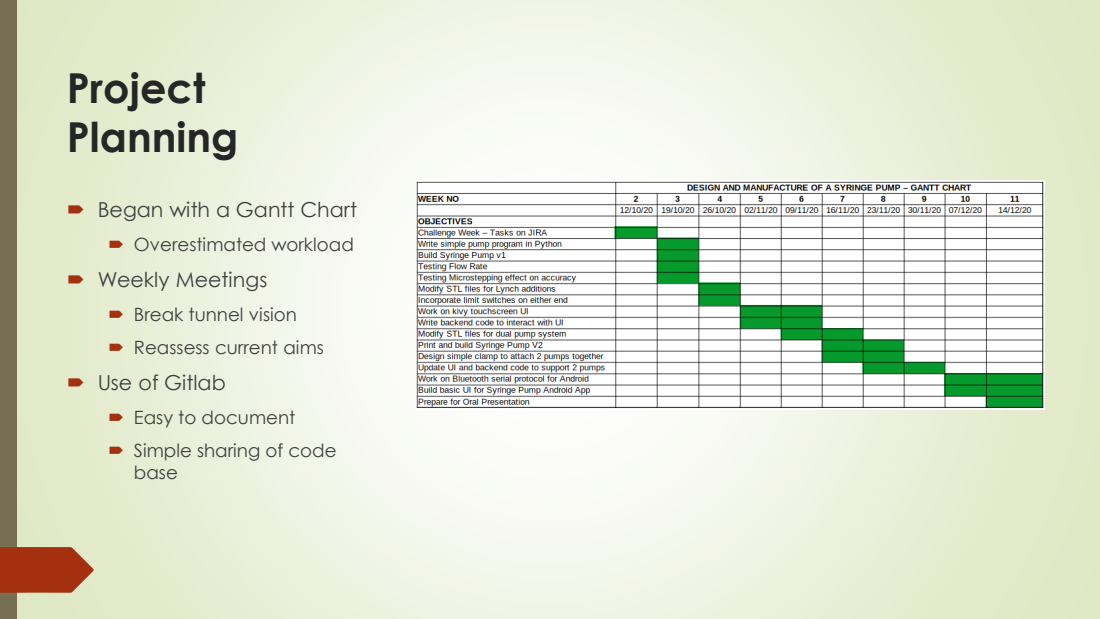
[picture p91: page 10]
Overestimated workload; Weekly Meetings

Began with a Gantt Chart

Break tunnel vision
Reassess current aims
Use of Gitlab

Easy to document
Simple sharing of code
base

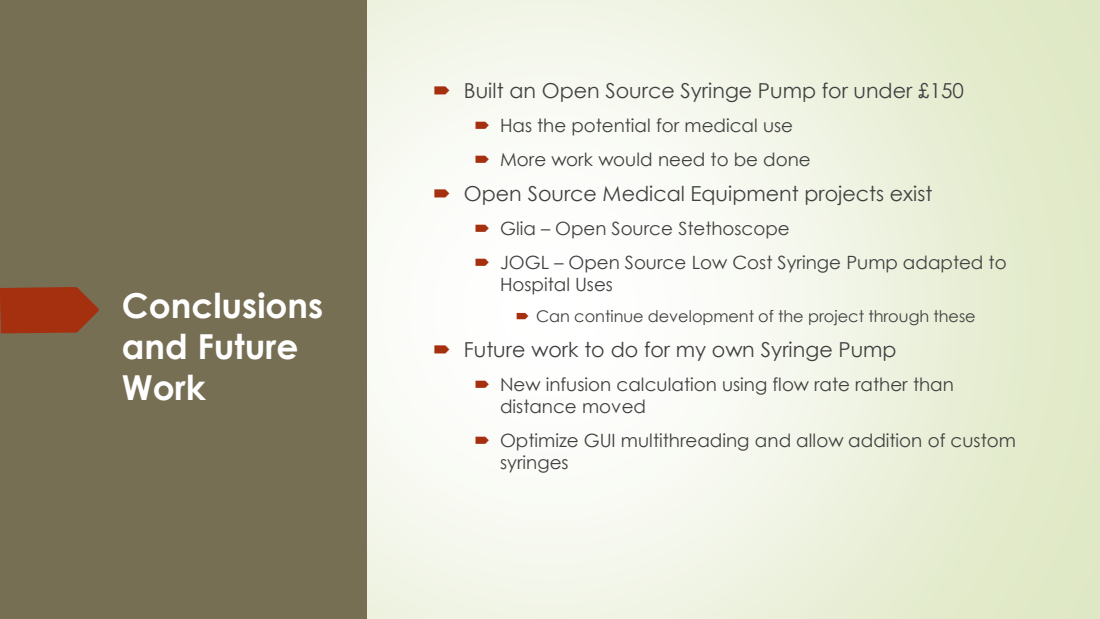
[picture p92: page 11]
Conclusions and Future Work

Built an Open Source Syringe Pump for under £150

Has the potential for medical use
More work would need to be done
Open Source Medical Equipment projects exist

Glia – Open Source Stethoscope
JOGL – Open Source Low Cost Syringe Pump adapted to
Hospital Uses

Can continue development of the project through these

Future work to do for my own Syringe Pump

New infusion calculation using flow rate rather than
distance moved
Optimize GUI multithreading and allow addition of custom
syringes

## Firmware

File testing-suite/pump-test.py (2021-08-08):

#!/usr/bin/python3
# pump_testing.py
#
# Set of functions for basic operations including
# - Single revolution with direction choice
# - Microstepping for each mode
# - Full length movement from end to end
# - Proper delay calculation (derivation will be availiable on GitLab)

from time import sleep
import RPi.GPIO as GPIO

DIR = 20
STEP = 21
#SPR = 200

CW = 1 # infuse
CCW = 0 # withdraw

MODE = (5,6,13)

FRONT_SW = 16
BACK_SW = 19

RESOLUTION = {'1':(0,0,0),
              '1/2':(1,0,0),
              '1/4':(0,1,0),
              '1/8':(1,1,0),
              '1/16':(1,1,1)}

STEPS = {'1':200,
         '1/2':400,
         '1/4':800,
         '1/8':1600,
         '1/16':3200}

DELAY = {'1':0.005,
         '1/2':0.005/2,
         '1/4':0.005/4,
         '1/8':0.005/8,
         '1/16':0.005/16}

MS = ['1','1/2','1/4','1/8','1/16']

def setup():
    GPIO.setwarnings(False) # DIR and STEP pins being reinitialised, so warnings show
    GPIO.setmode(GPIO.BCM)
    GPIO.setup(DIR, GPIO.OUT)
    GPIO.setup(STEP, GPIO.OUT)
    GPIO.setup(MODE, GPIO.OUT)
    GPIO.setup(FRONT_SW, GPIO.IN)
    GPIO.setup(BACK_SW, GPIO.IN)


# delay between .001 and .005 for full step (200) seems good

def revolution(dir, res):
    GPIO.output(DIR, dir)
    GPIO.output(MODE, RESOLUTION[res])
    for _ in range(STEPS[res]):
        GPIO.output(STEP, GPIO.HIGH)
        sleep(DELAY[res])
        GPIO.output(STEP, GPIO.LOW)
        sleep(DELAY[res])
    print("1 rev completed")

# microstep("1/2")
# would recalculate steps and delay, put into revolution

def microstep(dir, res):
    GPIO.output(MODE, RESOLUTION[res])
    revolution(dir, res)

def all_microsteps(dir):
    for key in MS:
        revolution(dir, key)
        sleep(0.5)

# testing the above functions
def test_1():
    for _ in range(50):
        microstep(CW,"1")
    all_microsteps(CW)
    # 1/4 - minimal vibration, lowest steps
    for _ in range(30):
        microstep(CW,"1/4")

# new operation functions, above is fine for tests but need something more suitable

# since this will be calculated by the program, will give its own function for now
# take ms as a string
# using the RESOLUTION dictionary to define pin outs
def set_microstep(ms):
    GPIO.output(MODE, RESOLUTION[ms])

# will take either variable: CW or CCW
# CW -> infuse
# CCW -> withdraw
def set_direction(dir):
    GPIO.output(DIR, dir)

# some extra functions i need for ease of testing

def withdraw_continuous():
    set_direction(CCW)
    set_microstep('1')
    while 1:
        GPIO.output(STEP, GPIO.HIGH)
        sleep(0.005/4) # smooth delay to reduce vibration
        GPIO.output(STEP, GPIO.LOW)
        sleep(0.005/4)

def infuse_continuous():
    set_direction(CW)
    set_microstep('1')
    while 1:
        GPIO.output(STEP, GPIO.HIGH)
        sleep(0.005/4)
        GPIO.output(STEP, GPIO.LOW)
        sleep(0.005/4)

# testing flow rate maths from project book
# taking into account syringe size, conversion rates, microstepping

# steps to infuse the entire syringe
# more efficient to pre-calculate these values
# BASED ON BD Plastipak Syringes

# 20ml
ms_to_steps_20 = {'1':17500, '1/2':35000, '1/4':70000, '1/8':140000, '1/16':280000}

# 60ml
ms_to_steps_60 = {'1':27250, '1/2':54500, '1/4':109000, '1/8':218000, '1/16':436000}

# combine these

ms_size_steps = {20:{'1':17500, '1/2':35000, '1/4':70000, '1/8':140000, '1/16':280000},
                 60:{'1':27250, '1/2':54500, '1/4':109000, '1/8':218000, '1/16':436000}}


# now the above for syringe pump v2

v2_ms_size_steps = {20:{'1':7000, '1/2':14000, '1/4':28000, '1/8':56000, '1/16':112000},
                    60:{'1':10900, '1/2':21800, '1/4':43600, '1/8':87200, '1/16':174400}}

# given microstepping value, time to infuse (seconds) and syringe size
# calculate the delay per step final delay will be halved, to delay
# before and after pin out signal
def calculate_delay(ms, infuse_time, syringe_size):
    if(syringe_size == 20):
        total_steps = ms_to_steps_20[ms]
    elif(syringe_size == 60):
        total_steps = ms_to_steps_60[ms]
    else:
        print("Invalid syringe size")
    delay = infuse_time/total_steps
    return delay


# dir -> variable : Infuse/withdraw the syringe
# ms -> String : Chosen microstepping value
# infuse_time -> int (seconds) : how long it should take
# syringe_size -> int : in mL,
def pump(dir, ms, infuse_time, syringe_size):
    # setup dir and ms
    set_direction(dir)
    set_microstep(ms)
    delay = calculate_delay(ms, infuse_time, syringe_size)
    if(syringe_size == 20):
        total_steps = ms_to_steps_20[ms]
    elif(syringe_size == 60):
        total_steps = ms_to_steps_60[ms]
    for _ in range(total_steps):
        GPIO.output(STEP, GPIO.HIGH)
        sleep(delay/2)
        GPIO.output(STEP, GPIO.LOW)
        sleep(delay/2)
    print("operation complete")

# test the calculate delay function in operation with pump
def test_2():
    # infuse 20ml in 1 minute, ms=1
    pump(CW, '1/2', 60, 20)
    print("test complete")

# limit switch testing

def infuse_continuous_switch():
    set_direction(CW)
    set_microstep('1')
    # while switch isnt pressed
    while(GPIO.input(FRONT_SW)):
        GPIO.output(STEP, GPIO.HIGH)
        sleep(0.005/4)
        GPIO.output(STEP, GPIO.LOW)
        sleep(0.005/4)

def withdraw_continuous_switch():
    set_direction(CCW)
    set_microstep('1')
    while(GPIO.input(BACK_SW)):
        GPIO.output(STEP, GPIO.HIGH)
        sleep(0.005/4)
        GPIO.output(STEP, GPIO.LOW)
        sleep(0.005/4)

if __name__ == "__main__":
    setup()
    #infuse_continuous()
    #test_1()
    #withdraw_continuous()
    #test_2()
    withdraw_continuous_switch()
    #infuse_continuous_switch()

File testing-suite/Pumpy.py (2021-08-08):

#!/usr/bin/python3
# Pumpy.py
#
# Class encapsulating setup and operation for operating the pump
# including properties and methods
#
# For easy operation of the pump within a GUI

"""
DESCRIPTION OF PIN OUTS

DIR - 20 : Set direction clockwise/counter-clockwise
STEP - 21 : Start/Stop movement of Stepper Motor

MS_MODE - (5,6,13) : 3 pins control microstepping level

MS_RESOLUTION - Dictionary of signals, applied to MS_MODE to set microstepping level
MS_SIZE_STEPS_V1 - <syringe-size(mL)>:{<ms-value>:<steps>}
                 - Given a syringe size and microstep value, return number of
                   steps to infuse the full syringe
MS_SIZE_STEPS_V2 - As above, but for Syringe Pump v2

INFUSE - 1 : CW movement
WITHDRAW - 0 : CCW movement

FRONT_SW - 16 : Limit Switch on Syringe Holder side (Labeled as 1)
BACK_SW - 19 : Limit Switch on Motor End - Variable distance (Labeled as 2)

"""

from time import sleep
import RPi.GPIO as GPIO

class Pumpy():

    INFUSE = 1 # CW
    WITHDRAW = 0 # CCW

    MS_RESOLUTION = {"1": (0,0,0),
                     "1/2": (1,0,0),
                     "1/4": (0,1,0),
                     "1/8": (1,1,0),
                     "1/16": (1,1,1)}

    MS_SIZE_STEPS_V1 = {20:{"1":17500, "1/2":35000, "1/4":70000, "1/8":140000, "1/16":280000},
                        60:{"1":27250, "1/2":54500, "1/4":109000, "1/8":218000, "1/16":436000}}

    MS_SIZE_STEPS_V2 = {20:{'1':7000, '1/2':14000, '1/4':28000, '1/8':56000, '1/16':112000},
                        60:{'1':10900, '1/2':21800, '1/4':43600, '1/8':87200, '1/16':174400}}

    def __init__(self, dir, step, ms1, ms2, ms3, f_switch, b_switch, spr=200):
        self.direction_pin = dir
        self.step_pin = step
        #self.microstep_1 = ms1
        #self.microstep_2 = ms2
        #self.microstep_3 = ms3
        self.mode = (ms1,ms2,ms3)
        self.spr = spr
        self.f_switch = f_switch
        self.b_switch = b_switch
        self.setup()

    def setup(self):
        GPIO.setwarnings(False)
        GPIO.setmode(GPIO.BCM)
        GPIO.setup(self.direction_pin, GPIO.OUT)
        GPIO.setup(self.step_pin, GPIO.OUT)
        GPIO.setup(self.mode, GPIO.OUT)
        GPIO.setup(self.f_switch, GPIO.IN)
        GPIO.setup(self.b_switch, GPIO.IN)

    # ms -> string ("1","1/2","1/4","1/8","1/16")
    def set_microstep(self, ms):
        GPIO.output(self.mode, self.MS_RESOLUTION[ms])

    # dir -> variable (INFUSE, WITHDRAW)
    def set_direction(self, dir):
        GPIO.output(self.direction_pin, dir)

    # dir -> variable (INFUSE, WITHDRAW)
    # as a stop condition, will use boolean
    # usign a while loop means no escaping
    def continuous(self, dir):
        self.set_direction(dir)
        self.set_microstep("1")

        if(dir == 0):
            check = self.b_switch
        else:
            check = self.f_switch

        while(GPIO.input(check)):
            GPIO.output(self.step_pin, GPIO.HIGH)
            sleep(0.005/4)
            GPIO.output(self.step_pin, GPIO.LOW)
            sleep(0.005/4)

    def stop(self):
        GPIO.output(self.step_pin, GPIO.LOW)
        Pumpy.END_CONT = True

    # infuse_time (int) (seconds)
    # syringe_size (int) (mL)
    # ms (string) ("1","1/2","1/4","1/8","1/16")
    def calculate_delay(self, infuse_time, syringe_size, ms):
        total_steps = self.MS_SIZE_STEPS_V2[syringe_size][ms]
        delay = infuse_time/total_steps
        return delay

    # dir -> variable (INFUSE, WITHDRAW)
    # infuse_time (int) (seconds)
    # syringe_size (int) (mL)
    # ms (string) ("1","1/2","1/4","1/8","1/16")
    def pump(self, dir, infuse_time, syringe_size, ms):
        self.set_direction(dir)
        self.set_microstep(ms)
        delay = self.calculate_delay(infuse_time, syringe_size, ms)
        total_steps = self.MS_SIZE_STEPS_V2[syringe_size][ms]
        for _ in range(total_steps):
            GPIO.output(self.step_pin, GPIO.HIGH)
            sleep(delay/2)
            GPIO.output(self.step_pin, GPIO.LOW)
            sleep(delay/2)

if __name__ == "__main__":
    pump = Pumpy(20,21,5,6,13,16,19)
    #pump.setup()
    # infuse, in 60s, 20mL, with microstepping level 1
    #pump.pump(INFUSE,60,20,"1")
    pump.continuous(Pumpy.INFUSE)
    #sleep(5)
    #pump.stop()
